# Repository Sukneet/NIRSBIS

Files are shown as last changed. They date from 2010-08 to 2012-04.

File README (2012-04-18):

Design of a Near Infrared Spectrophotometry Brain Imaging System

Measuring brain activity is at task generally left for EEG or fMRI. However, there is a lesser known imaging technique known as near infrared spectrophotometry in which near infrared light is shone into the patients head to measure changes in oxygenation that directly relates to brain activity. This paper describes a low-cost, wireless, portable near infrared spectrophotometry system that is able to measure brain activity. The results show that not only is the system able to measure changes in brain activity relating to motor movement, visual stimulation, and intense thinking, but it is also able to measure muscle activity.

My final year capstone project. Hosted for archival reasons.

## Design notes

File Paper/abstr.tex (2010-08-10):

\prefacesection{Abstract}

Measuring brain activity is at task generally left for EEG or fMRI. However, there is a lesser known imaging technique known as near infrared spectrophotometry, in which near infrared light is shown into the patients head to measure changes in oxygenation that directly relate to brain activity. This paper describes a low-cost, wireless, portable  near infrared spectrophotometry system that is able to measure brain activity. The results show that not able is the system able to measure changes in brain activity relating to motor movement, visual stimulation, and intense thinking, it is also able to measure muscle activity. 

\vspace{10mm}

\noindent Keywords: near-infrared spectroscopy, brain activity, functional monitoring and imaging, imaging, optical imaging

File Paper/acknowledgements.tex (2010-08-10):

\prefacesection{Acknowledgements}

The author would like to thank Dr. Doyle, this project's faculty adviser, for his various advice and directions. Texas instruments deserves acknowledgement for supplying samples of the microcontroller, LDO regulator, monolithic photodiode, and other components. Dupont generously supplied a large sample of Pyralux flexible PCB. Additionally, the author would like to thank Atsuko Sugahara, at Marubeni Corporation, for spending the time to find the required infrared LEDs and allowing for the purchase of them in low quantity. 

The developers behind the mspgcc project deserve a large thank you for porting the GCC toolchain to the MSP430 and creating various helpful programs. The developers at TinyOS also deserve acknowledgement for creating the software to program the MSP430 through its bootloader.

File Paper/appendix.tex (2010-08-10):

\appendix

\chapter {Calculations}

\section {Minimum UART speed calculation}

Given 2 sensors and a time resolution of 10ms (refer to Figure 4.9),

\begin{equation}
\frac{10\ ms}{12\ parts} \div 4\ parts = 4800\ Hz
\end{equation}
\begin{equation}
\frac {4800} {s} \times 16\ bits = 76\ 800\ bit/s
\end{equation}

\section {DPF calculation}

The differential path length factor (DPF) can be calculated from the following equation \cite{rosen05}

\begin{equation}
DPF^\lambda = \frac{1}{2}\left(\frac{3\mu_{s}^\lambda}{\mu_{a}^\lambda}\right)^{1/2} \left(1-\frac{1}{1+d(3\mu_{s}^\lambda\mu_{a}^\lambda)^{1/2}}\right)
\end{equation}

The absorption ($\mu_{a}^\lambda$) and reduced scattering ($\mu_{s}^\lambda$) coefficients cannot be directly measured by near infrared light, so the values given in past studies will be used. Specifically, $\mu_{a}^{730nm}$=0.015 mm$^{-1}$, $\mu_{a}^{850nm}$ = 0.023 mm$^{-1}$, $\mu_{s}^{730nm}$= 0.80 mm$^{-1}$, and $\mu_{s}^{850nm}$=0.95 mm$^{-1}$. The values at 750nm could not be found, so the values at 730nm will be used. Plugging these values into the equation above gives, $DPF^{730nm}$=5.0055 and $DPF^{850nm}$=4.6564.

\chapter{Flow Charts}
\section {Microcontroller code flow chart}

\headsep = 5pt
\begin{figure}[htp]
\centering
\caption{Microcontroller code flow chart}

\end{figure}

\begin{figure}[htp]
\centering

\end{figure}

\begin{figure}[htp]
\centering

\end{figure}

\begin{figure}[htp]
\centering
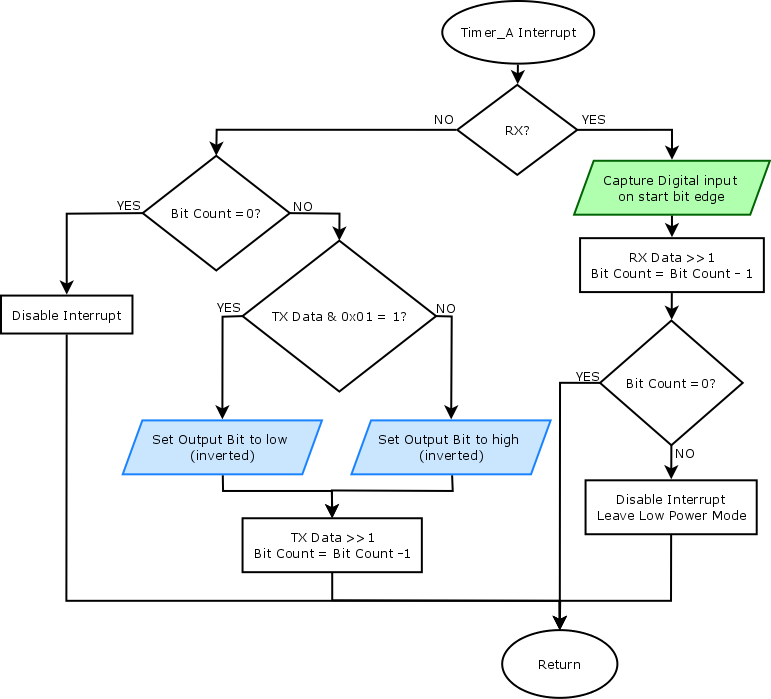
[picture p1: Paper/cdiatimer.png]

\caption{Timer\_A interrupt flow chart}
\end{figure}

\headsep = 0.5in

\chapter {Matlab Source Code}
\lstinputlisting[language=Matlab,breaklines=true]{filter.m}

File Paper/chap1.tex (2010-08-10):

\chapter{Introduction}
\section{Background}
Near-infrared spectrophotometry (NIRS) is a non-invasive imaging technique that can be used to measure brain function. It provides a higher spatial resolution than EEG or MEG without subjecting the patient to radiation in PET or having the low temporal resolution in fMRI scans \cite{wolf08}. NIRS systems are also considerably more portable than PET or fMRI scanners without the messy string of wires involved with EEG or MEG. As such, they can be used on bed-ridden patients where transportation is not possible. NIRS systems can also be used for long periods and are not directly susceptible to electro-magnetic interference  \cite{wolf08}.  \cite{wolf08} provides a good discussion about the principles, applications, and technologies of NIRS. 

A NIRS system for measuring brain activity is of particular interest in neonatal brain activity measurement where fMRI is not recommended for use \cite{wolf08}. Such systems allow for the quantification of the haemodynamic response of the cortex to visual, tactile, or auditory stimuli \cite{mini08}.  

NIRS works on the principle that light passing through a tissue is variably attenuated depending on the constitution of the tissue \cite{wolf08}. A near-infrared light source (within the spectra 700nm - 900nm) is placed onto the tissue. The re-emergent light is then picked up by a detector and the light intensity is measured. Varying levels in oxyhaemoglobin (O$_{2}$Hb) and  deoxyhaemoglobin (HHb) cause the optical properties of the tissue to vary; the absorption and scattering of light passing though the tissue changes. NIRS is very sensitive to these changes and is, thus, able to measure the haemoglobin concentration in the order of per mills \cite{wolf05}.

NIRS is able to pick up fast neuronal signals and slow haemodynamic signals. It is currently the only available imaging technique that is able to detect both signals, which is its main advantage. Fast neuronal signals are changes directly associated with neuron activity. The response typically arrives within 200ms. Slow haemodynamic signals are changes in haemoglobin concentrations caused by an increase in local oxygen use and subsequently blood flow due to brain activity \cite{mini08}. Fast neuronal signals are typically measured by EEGs, while slow haemodynamic signals are typically measured by fMRI.

A Near-Infrared spectrophotometry system was selected as this paper's subject because it combines three of the author's interests; imaging, optics, and the brain. Additionally, the project could be done fairly cost effectively, costing roughly \$200-300.

\section{Definition}
The main scope of this project is to measure brain activity in a patient. In order to do this, near infrared spectrophotometry will be used, wherein near-infrared light is shown into the patient's head to measure changes of oxygenation that directly relate to brain activity.

The objective of this project is to design a near infrared spectrophotometry (NIRS) system for the measurement of brain activity in localized areas in the brain. A prototype of the design will be built and wirelessly interfaced with a computer. The time-varying haemodynamic signals will then be plotted on the computer versus time. 

It is important to note that the results will be qualitative rather than quantitative as a device that correctly measures the optical properties of the patients skin, skull, fat, etc is not in the scope of this project. Since these optical properties vary based on skin pigmentation, age, gender, and many other factors, such a device is needed to obtain exact quantitative measurements. However, without this device a NIRS system can still measure varying haemodynamic signals. The absolute haemodynamic signal values will be irrelevant, the change in the haemodynamic signals over time are the relevant measurements. 

Since a major target of NIRS systems are neonatal infants, it is critical to minimize distress by performing the measurements as comfortably as possible due to the frailty of newborns \cite{mini08}. This is achieved by not having wires attached from the system to a computer, so as to not confine movement. Additionally, since neonatal infants are small, the system should also be small and light to restrict the infant as little as possible. As such, the device should be portable, light, small, and wireless. 

Additionally, a portable, light, small, wireless device allows the device to used on freely moving subjects. This allows the device to measure brain activity in athletes during exercise, subjects in social environments, and in animals.  

As with most projects, especially at the undergraduate level, it is important to keep costs down. Since NIRS systems for brain imaging is a fairly new field with no currently available commercial systems, low-cost devices will help to bring NIRS devices to the general population. In order to compete with current EEG systems, the device has to be fairly cheap and affordable. Therefore, while many early NIRS systems required the use of lasers, this project will focus on using low-cost LEDs.

Safety is always a concern in any device, specifically in medical equipment. The use of LEDs help to make NIRS systems suitable for clinical environments. The use of Lasers in early systems brought in safety concerns pertaining to damage the eye.

Thus, this project will focus on building a prototype of a low-cost wireless, portable NIRS system that is able to measure the change in haemodynamic signals.

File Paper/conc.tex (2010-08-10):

\chapter {Recommendations}

There are quite a few improvements that can be made to the system that were mainly not implemented due to time constraints and/or unexpected problems.

LED light and photodiode insulation is a topic that was not addressed in this system. To increase the SNR of the system it is advisable to block outside sources of light from interfering with the measurements or light sources. It is advisable to use some form of black insulation to absorb the outside light rather than reflect it to reduce scattering and increase SNR. 

One way of doing this is to apply black epoxy around the LEDs and photodiodes sufficiently to block light leakage and external light. However, sourcing medical grade black epoxy is not an easy task; it is hard enough finding normal black epoxy. It is possible to add a pigment to white epoxy, but this is no easy task either. An alternative is to use some kind of black foam or mesh.

The design of the sensor is not ideal. If it were to be revised a double-sided PCB would be used or the sensor would be made larger to reduce the number of jumper wires. This would help to make the sensor more robust and make building the sensor easier. Additionally the traces would be made larger to reduce the chance of breakage when flexed. 

The LEDs do not rest against the patient's skin when the sensor is placed against the patient. This reduced the SNR of the system by allowing light in from outside sources and decreases the light intensity before reaching the area of interest. This was the unattended side-affect of using SMD LEDs with the OPT101 monolithic photodiodes. Perhaps the use of standard SMD photodiodes or non-SMD LEDs would fix this. However, the use of standard SMD photodiodes would require the addition of a transimpedance amplifier. Finding non-SMD LEDs would be hard task, the SMD LEDs were selected in this project because that was all that could be acquired for a reasonable price. 

Attaching the sensors to the patients head was not addressed in this project. This is more or less a luxury. For the testing phase it is somewhat sufficient to hold the sensors to the head by hand. This will not be suitable for the final product though; any movement from the area of interest will add noise into the measurements. Thus, current ideas for achieving this would be using something like a headband or hairband to hold the sensor down; something that would provide enough pressure to ensure the sensor doesn't move while still allowing comfort for the patient.

Currently, this microcontroller uses BJTs to control the infrared LEDS. Should a second revision be done, an LED driver which controls the LEDs by PWM (pulse width modulation) would be used rather than simple BJTs. This will increase the efficiency of the system and allow greater control over the LEDs. This would allow for more localized measurements and power savings. Being able to control the brightness of the LEDs can be very advantageous for a versatile system. It does, however, come at the cost of complexity and thus time.

The overall system would greatly benefit if the system could display the data in real time. This is not very hard to do, just time consuming. Though having this would be of great benefit in a clinical environment where seeing the results the as fast possible may save life. 

Perhaps the greatest downfall of this project was trying to accomplish too much in a short period of time. The author took on the task of designing everything from scratch. This may have been detrimental to the overall result of the project. Rather than spending time on correctly displaying the results or ensuring the system work correctly all the time, time was spent make the microcontroller. It probably would have been beneficial to the project to have used an existing embedded system and focus more on the overall result. However, the knowledge gained has been invaluable to the author and the experience obtained designing the microcontroller will more likely be more beneficial to the author in the long run.

\chapter {Conclusion}

Despite these limitations, a fairly low-cost, wireless portable Near Infrared Spectrophotometry system was successfully built that is able to measure haemodynamic signals. The results shown by the NIRS device created in this project are promising. It was able to measure brain activity in the brain not only during motor activity, but during intense thinking and visual stimulation. The results are fairly promising as well, there is a strong correlation between brain activity and the measurements taken. In addition, it is also able to directly measure muscle activity, which was an unexpected bonus. 

While NIRS devices are currently still in the research phase with very few commercial systems, it is hard to see it ever successfully replacing EEG or fMRI measurements. EEG systems have a very large marketshare with commercially available system everywhere for very cheap and have a slightly higher temporal resolution than NIRS. fMRI has a much higher spatial resolution than NIRS, at the cost of temporal resolution, but there are many times researchers or doctors need to see brain activity deep into the brain. Laser NIRS systems can penetrate deeper than LED based ones, but at an increased cost, complexity, and loss of portability. However, there is that niche market where EEG does not cut it due to electromagnetic interference or a device with spatial resolution is required but fMRI is deemed to costly, is unable to be used due to long waiting lists, or in the case the patient cannot be transferred to the MRI machine. For this niche market, NIRS is their saviour.

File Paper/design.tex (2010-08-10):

\chapter{Design Procedures}

To create the NIRS system, a sensor consisting of LEDs, to emit light through the area of interest, and photodiodes, to convert the transmitted incident light into an electrical signal, must be made. The signal from the photodiodes must then be connected to an ADC in order to convert the analog signal to a digital signal that is readable by the computer doing the calculations. The digital signal must then be transmitted to the computer where calculations would be done.

To control the LEDs and convert the analog signal to a digital one, a microcontroller will be used. The microcontroller will then be interfaced to a computer through UART, initially through USB, then finally wirelessly through Bluetooth. The overall system can be seen in Figure 4.1.

\begin{figure}[htp]
\centering
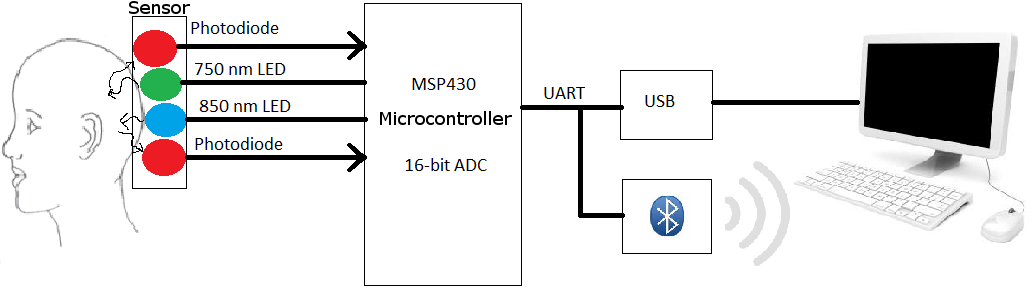
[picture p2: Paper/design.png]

\caption[A very basic overview of the system.]{A very basic overview of the system. For the testing phase, USB will be used to communicate with the computer. Eventually, Bluetooth will be used as the primary means of communication.}
\end{figure}

Bluetooth was selected over a low power wireless interface, such as ZigBee, due to Bluetooth being widely available on all modern phones. It was the intention to interface the device with a mobile phone, time permitting. However, this was never done. Bluetooth consumes much more power than other competing wireless communication systems, so to obtain optimum battery life it is not ideal. Had the author realized that there would be no time to interface the device with a mobile phone, a lower power wireless communication system would have been selected, most probably ZigBee.

To design the NIRS system, it was decided to design everything from scratch. The microcontroller circuit, the sensor, as well as the software was designed and built/written. This was done to truly test the author's knowledge obtained from his years at McMaster University. Additionally, this project provided an excellent chance to be introduced to microcontroller circuit design.

Development of this system began with the microcontroller, since nothing would work without it, followed by the sensor, then finally the software.

\section{The Microcontroller}

The microcontroller selected for use in this project is the Texas Instruments MSP430, specifically the MSP430f4250. The MSP430 was chosen due to its low power requirements and 16-bit sigma-delta ADC. In most cases, a 12-bit ADC would be sufficient, but a higher resolution will allow for the weak temporal signals to be detected easier. The MSP430 is also fairly cheap. These characteristics make it ideal for this project and made it standout from other competitors. 

While the MSP430f4250 is slightly excessive for this project, due to its built in LCD controller and array of I/O ports, it was the cheapest MSP430 model that the minimum required I/O ports and a 16-bit ADC.

While the MSP430f4250 does not have any dedicated UART hardware on-board, a software timer UART is sufficient in this project. The project only requires samples to be transmitted from the microcontroller to a computer. It was decided that flow control was not necessary for this project. This decision, however, led to many problems during testing, which will be discussed later. 

To design the microcontroller circuit, datasheets, user guides, application notes, and reference designs were read and used as a basis. Thankfully, the MSP430 has many built in capacitors and resistors (for example, adjustable oscillator capacitors) that help to reduce the overall components of the  build. The schematic of the device can be seen in Figure 4.2

\begin{figure}[htp]
\centering
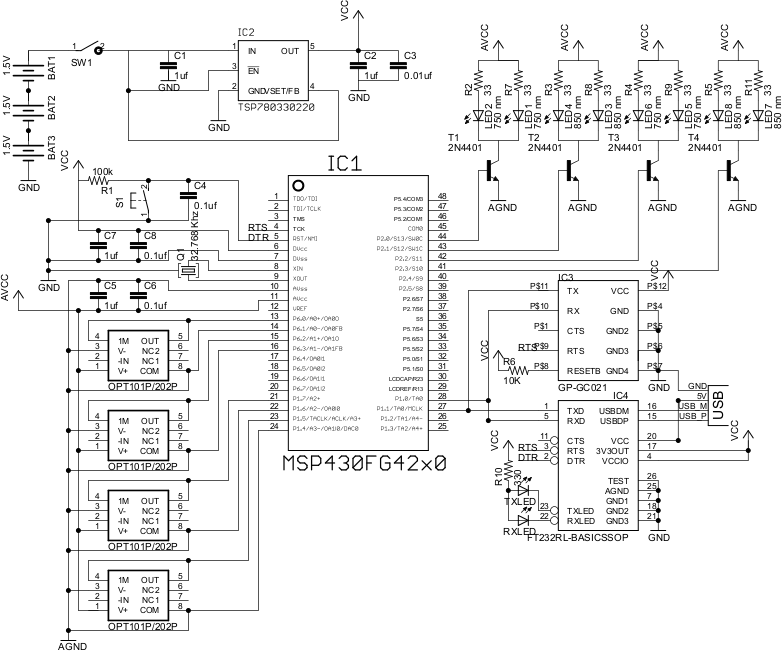
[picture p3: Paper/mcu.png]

\caption[Schematic of the system]{The schematic of the overall system. Note that two sensors are included in the diagram. The TPS79433 LDO regulator was used instead of the TPS780330220 in the diagram}
\end{figure}

A 32.768 Khz crystal is used because that is the only crystal the MSP430f4250 is designed to use. It is used as somewhat as a watchdog timer, waking the MSP430 up at select intervals to see if there is work to be done, unless it is told otherwise. Capacitors between VCC and GND were placed as close the the microcontroller as possible, as per Dr. Doyle's suggestion. This helps to reduce any noise that may have been picked up between the power supply and the microcontroller. This is especially a problem with the MSP430, any fluctuations/noise in the power supplied to it will cause the ADC to be very noisy. This is perhaps the main reason why the MSP430 is not very popular in projects that require signal acquisition. However, with proper consideration, this should not be much of an issue. To further reduce the noise in the ADC, separate power and ground are used for digital signals and analog signals, VCC \& GND and AVCC \& AGND respectively. 

The frequency the microcontroller operates at is governed by the voltage supplied by its power supply. Since the Bluetooth module operates at 3.3V and the USB UART device outputs power at 3.3V when powered by USB, a 3.3V power supply was selected. This sets the frequency of the microcontroller to ~7 Mhz, which is set by a FLL (frequency-locked loop). The speed the microcontroller operates at is of no big importance in this project. The sampling rate for data acquisition is slow enough, at 100Hz, that the 32Khz crystal is fast enough to supply the clock at which to sample the data. The speed of the UART is what is affected by the microcontroller speed. It was determined that the speed of the UART must be at least 76 800 bit/s or 76.8k baud (see Appendix A), which is easily exceed with a clock ~7Mhz.

To supply this voltage, 3 AA batteries connected to a regulator were chosen for long battery life. An LDO (low-dropout) regulator was selected over a more traditional regulator, such as an LM317. An LDO regulator was chosen because LDO regulators are highly efficient, consume very little power, and have low quiescent current, increasing battery life. Due to the the low power-requirements of every component, not much current is required by the system, making an LDO regulator ideal for use. LDO regulators are limited to the amount of current they can output due to consuming very little power.

The LDO regulator selected to do the job is the Texas Instruments TPS79433. It outputs voltages at 3.3V at a maximum current of 250mA. Additionally, it can be supplied power at less than 3.3V and will still output power at 3.3V. This is a nice feature because when the batteries drain to below 3.3V, the unit will still be operational. This regulator was selected because it meets all the requirements and free samples were obtainable from Texas Instruments. The circuit for the power supply was derived from the datasheet. 

To interface with the computer, the an USB to UART device was used. The FTDI FT232 was selected due to many good reviews on the device and good compatibility with Linux and Windows. The circuit design is based on the reference design given in the datasheet. One thing to note is that, while the built-in bootloader implemented flow control, which was necessary to invoke the bootloader, the software UART used in this project did not. As such, the DTR wire had to be disconnected from the microcontroller when not programming the device. Otherwise, the DTR wire would reset the device when communicating with the computer. The USB UART interface was used to program the device and initially communicate to the device during testing.

Once everything was deemed working, the Bluetooth module was added to interface with the computer. The Bluetooth module selected was RF-BTMX417 by MDFLY. This was selected due to its cheap price, Bluetooth 2.0 specifications, and low power requirements. The design for the Bluetooth module was based on the reference design in the datasheet.

Once all the parts were selected, the majority of the necessary parts were ordered from Digikey due to their cheap prices. Free samples were obtained of the microcontroller and LDO regulator from Texas Instruments. The Bluetooth module was ordered from ebay. The prototype was built on a breadboard using SMD to DIP adaptors for each component needing one. The prototype can be seen in figure 4.3

\begin{figure}[htp]
\centering
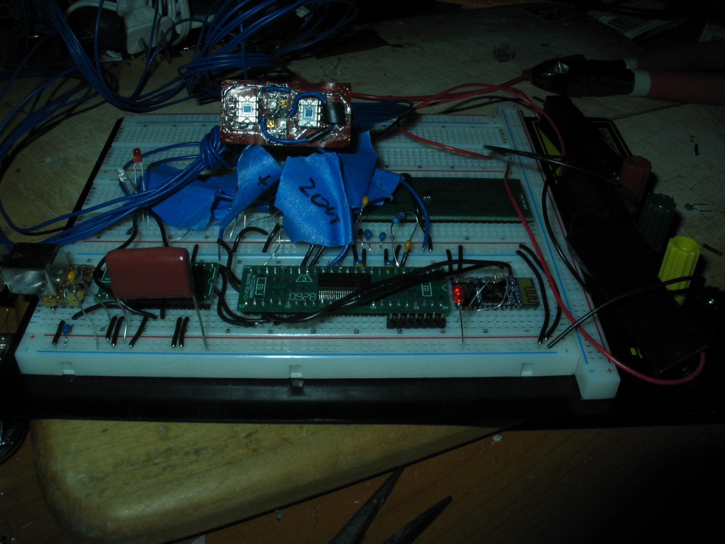
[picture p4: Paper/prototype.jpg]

\caption[The Prototype]{Picture of the prototype}
\end{figure}

To program the device, the MSP430f4250 has a a built-in non-overwritable (without JTAG) bootloader that can be programming over UART. A JTAG programmer would have cost at least \$100, greatly increasing the cost of this project, though making debugging much easier. The mspgcc tools included software, written by developers at TinyOS, to write to the bootloader on the MSP430. The mspgcc toolchain was used to compile the software, specifically mspgcc-4.4.3, and then programed to the device using the TinyOS software.

\section{The Sensor}

The sensor was first designed by selecting the components. The main problem was sourcing the LEDs with the desired wavelengths. After many emails to various distributors and manufactures, it was discovered Marubeni Corporation sold 750nm SMD LEDs in low quantities. The epitex SMT750-25 to be exact. As such, 750 nm LEDs were selected as one light source.

The wavelength of the other LED light source, must be above 800nm and be such that it minimizes interference between the two LEDs. Based on the study done in [4], the LEDs with wavelengths of 750nm and 850nm were selected to minimize interference between each LED. The 750nm wavelength responds better to deoxygenation in the blood and the 850nm wavelength responds better to oxygenation in the blood. Luckily enough, the 850nm LEDs were easily sourceable from Digikey in SMD form. The OSRAM SFH4650 being the only 850nm LED easily obtainable, or rather only 800 - 870nm SMD LED easily obtainable. The OSRAM SFH4650 has very recently been replaced by the more efficient SFH4651, while still providing similar specifications.

Unfortunately, the spectral half width of the LEDs are broader than desired. The 750nm LEDs have a spectral half-width of $\pm$ 35nm. While the 850nm LEDs have a spectral half-width of $\pm$ 42nm. This means the effective wavelength may vary by the spectral half-width, causing cross-talk between the LEDs and possibly throwing off the calculations. They have narrow halfangles, however, $\pm$ 25$^\circ$ and $\pm$ 20$^\circ$, respectively, which is desired to limit light leakage and force the highest light intensity towards the area of interest. With a forward current of 100mA, it is assumed the approximate penetration depth of these LEDs is 1cm, based on past studies \cite{rosen05}.

The LEDs are the most power-hungry device in this system. They could not be directly driven by the microcontroller. NPN transistors were selected to do this task. Specifically, the 2N4401 600mA NPN general purpose transistor. The 2N4401 was selected as it was the cheapest transistor available at Digikey with greater than 200mA continuous collector current. Each led has a maximum forward current of 100mA, so to power the LEDs at their maximum intensity, a 200mA transistor would be needed. The microcontroller would turn the NPN transistor on when it was desired to turn its subsequent LED on. Setting the Base of the NPN transistor to high, would allow current to flow from the Collector to the Emitter. Setting the Base to low (GND), would stop the current from flowing from the collector to the emitter. For a high integration density, each sensor and each transistor would have 2 LEDs of the same wavelength. This can be seen in Figure 4.4.

\begin{figure}[htp]
\centering
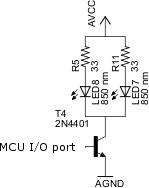
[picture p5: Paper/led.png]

\caption[LED control diagram]{The schematic of controlling one wavelength of LED on the sensor}
\end{figure}

To detect the reflected light back, a photodiode must be used. However, the electrical signal measured by a photodiode varies in current, opposed to voltage as most ADCs work. As such, the current must be converted into corresponding voltage by a transimpedance amplifier. An interesting solution to this problem is the OPT101 by Burr-Brown. It is a monolithic photodiode with a built-in transimpedance amplifier, all in a small DIP-8 package. This makes it ideal for this project. Two photodiodes are placed on each sensor to pick up scattering and increase the overall surface area of the detectors.

The overall design of the sensor can be seen in Figure 4.5. It was decided that the transistors would be put on the PCB rather than on the sensor to reduce the size of the sensor.

\begin{figure}[htp]
\centering

\caption[Sensor schematic]{The schematic of one sensor.}
\end{figure}

\subsection {Building the sensor}

Building the sensor was a daunting and hard task. The sensor had to be flexible to adhere to the head of the patient. As such, a flexible PCB is desired over a ridged one. 

To create the flexible PCB, the toner transfer method of homemade PCB creation was used. The PCB mill in the IEEE student Branch is not able to mill such a thin layer of copper on a flexible surface, and especially not with such thin tracings. 

The basic idea behind the toner transfer method is to print the design onto glossy paper using a laser printer. Melt the toner onto the copper board using an iron or something equally hot. Then etch the board using an enchant such as Ferric Chloride. Then to remove the toner from the PCB using a solvent such as acetone.

Dupont generously supplied a sample of dual sided Pyralux Copper PCB. However, making dual sided PCBs is no trivial task using the toner transfer method. My initial attempts to do so proved fatal. As such, one side was used a a ground plane, while the other side was etched. Since the LEDs were surface mount, all the devices had to be surface mount, unless they were to be mounted on the opposite side. 

To create the toner mask, Cadsoft EAGLE was used. The schematic was laid out in EAGLE, then the PCB designed. The idea was to minimize the size, keep the LEDs as close to the photodiodes as possible, and keep the parts somewhat symmetric to its double, while only making traces on one side. This layout sets the source-detector distance to be about 1cm (needed solve equations 3.7 and 3.8). The result can be seen in Figure 4.6.

\begin{figure}[htp]
\centering
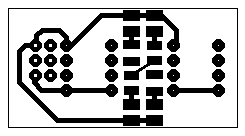
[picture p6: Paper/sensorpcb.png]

\caption[Sensor pcb layout]{The pcb layout of the  sensor, not mirrored.}
\end{figure}

The layout was then mirrored and printed out onto thick glossy photo paper (Staples Photo Plus Gloss Paper to be exact) using a Brother laser printer with toner usage set to high. The Brother laser printer is all that I had on hand, an older model laser printer would have been ideal since the Brother laser printer toner have a high melting point, making it hard to melt the toner from the paper onto the copper. The glossy paper was then placed onto the copper board and ironed with a standard household clothes iron set to high. The iron was left on for about 15 minutes. After which, the iron was removed and the copper board placed into water to separate the paper from it. After about 10 minutes, the remaining paper was peeled off of the copper board by hand. 

The toner was now stuck to the copper board. Any broken traces were touched up with a Sharpie marker. The opposite side (the ground plane) was coloured black to prevent the enchant from eating away at it. The board was then submerged in the etching solution (Ferric Chloride) to remove the exposed copper. After about 20 minutes, the exposed copper was removed and the board fully etched. The board was then rinsed off in water and cleaned up with acetone to remove the toner and Sharpie marker from the board. Any extra copper traces were scraped off. Solder was placed onto the copper traces to prevent oxidation and make soldering the components easier. The PCB was then complete as can be seen in Figure 4.7.

\begin{figure}[htp]
\centering
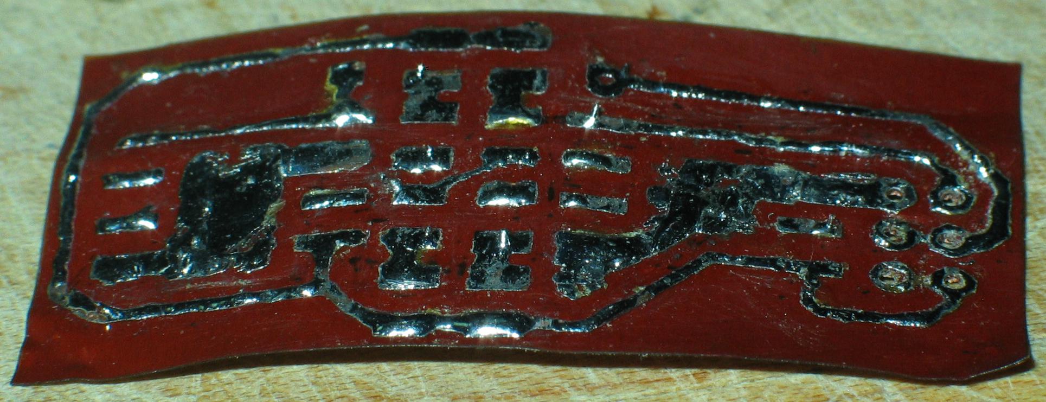
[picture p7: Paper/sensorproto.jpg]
\subfigure[Sensor after etching]{ }
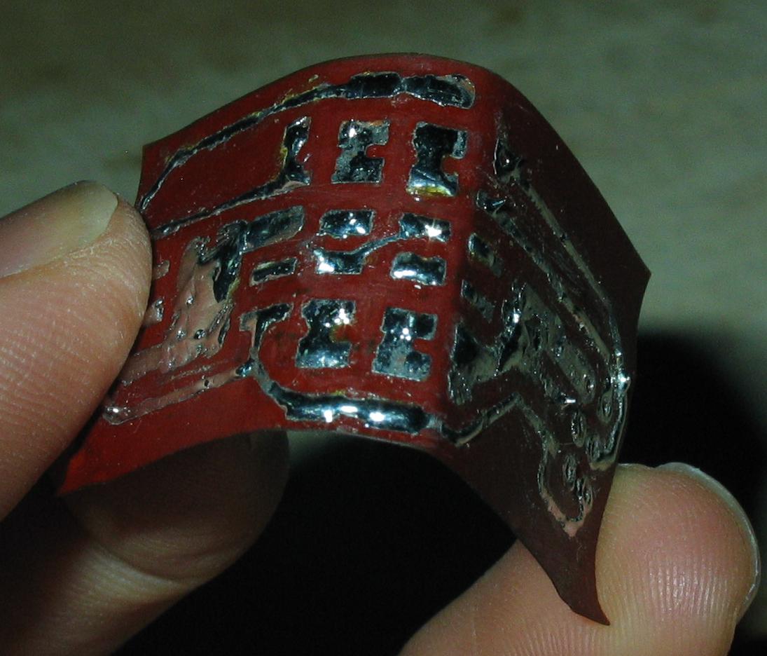
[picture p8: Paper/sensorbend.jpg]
\subfigure[Sensor showing flexibility]{ }
\caption[Sensor prototype PCB]{The completed sensor PCB}
\end{figure}

Unfortunately, I made the traces to thin. While the came out okay out of the etchant, after many bends, some traces broke (even though they appeared fine). 

Again, the majority of the electrical components were obtained from Digikey. With the exception of the OPT101 monolithic photodiode, which was obtained from Texas Instruments as a free sample. After populating the sensor and difficult task of adding jumper wires, the finalized sensor prototype was complete. Correctly building the board took quite a few hours to complete. The complete sensor can be seen in Figure 4.8. Due to time constraints only 1 sensor was built. Though, the microcontroller was designed to handle 2.

\begin{figure}[htp]
\centering
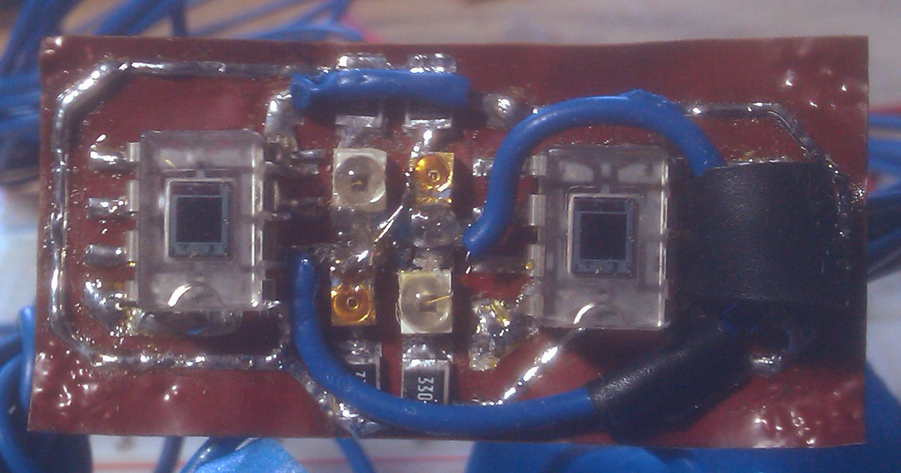
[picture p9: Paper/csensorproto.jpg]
\subfigure[Complete Sensor Prototype]{ }
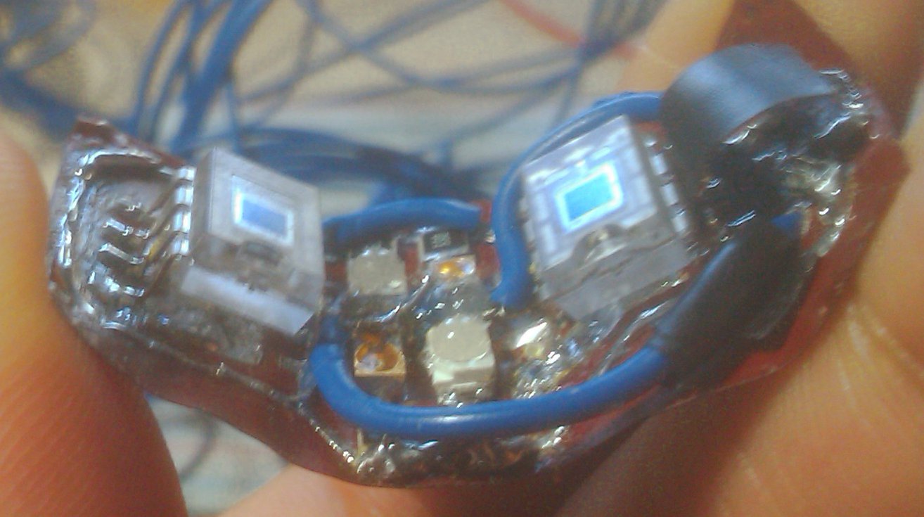
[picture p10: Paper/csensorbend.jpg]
\subfigure[Sensor Prototype showing flexibility]{ }
\caption[Finalized Sensor Prototype]{The finalized complete sensor}
\end{figure}

\section{Software}

To write the software for the microcontroller, C was selected over assembly to reduce development time and increase readability. As discussed above, the UART function had to be written in software in addition to data acquisition. To do this, example timer UART code by L. Westlund at Texas Instruments, available in the IAR Embedded Workbench example files, was used as a basis for the software UART functionality. This was done because the author did not know how to implement the UART functionality from scratch. Once UART was working, data acquisition was tackled.

\subsection{Data Acquisition}
Due to the slow haemodynamic response in your brain due to activity, a time resolution of 10ms (or 100Hz) is all that is needed. That is all the wavelengths and positions must be sampled at least every 10 ms.

To do this, data is sampled in a time multiplexed fashion. That is, all the data is sampled independently in a certain order within the time resolution. 

Firstly the sensors are sampled with all the LEDs off to obtain the background light intensity. Then the first wavelength of LED is turned on and allowed to stabilize for a period of time. Then the first signal is obtained from the first OPT101 photodiode, subtracted by the background light intensity, and transmitted to the computer.  Then the second signal is obtained from the second OPT101 photodiode, subtracted by the background light intensity, and transmitted to the computer. Then the LEDs are turned off, the second wavelength LEDs turned on, allowed to stabilize, and the cycle repeated. Once this cycle is completed, all the LEDs are turned off, the background light intensity sampled, and the cycle repeats. This is illustrated in Figure 4.9. Though, perhaps it is more easily seen in the microcontroller code flow chart in Appendix B.1.

\begin{figure}[htp]
\centering
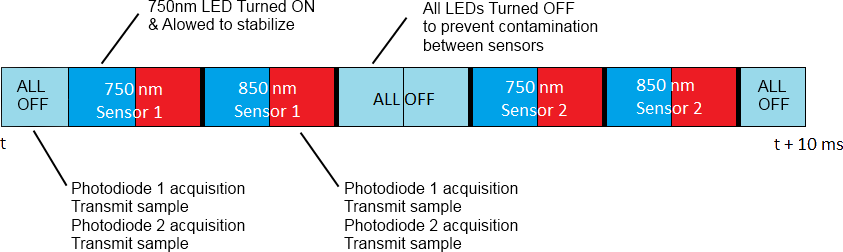
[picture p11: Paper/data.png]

\caption[Time multiplexed acquisition]{An illustration of the time multiplexed acquisition cycle.}
\end{figure}

\subsection {Computer Software}

To write the software, Ruby was selected as the language of choice. It was selected due to the author's desire to learn Ruby as it is a very popular dynamic general purpose object-oriented programming language. It is spoken highly of by many experienced computer science veterans. While not up to the speed of C or C++, Ruby has amazingly good performance for a dynamic programming language.

The computer software must firstly obtain the data from the device. To do this the serialport library from rubygems (a host of many Ruby librarys or 'gems') was used to interact with the serial port on the computer, communicating through UART. The serial port is opened, sent the message 'S', to message the device to begin acquiring data. The program then receives the data. The data is split into two parts the upper 8 bit and the lower 8 bits when it is received. The program combines them together and divides the resulting value by 0xFFFF. The reason for this is the output from the ADC on the microcontroller is relative to its maximum value of 0xFFFF. To ensure the data arrives correctly, an 'S' is transmitted by the device before sending each set of data to ensure that the device is synchronized correctly with the computer. Once all the data is received, the calculations are done on the raw data to obtain the necessary relevant values.

Equations 3.7 and 3.8 were used to calculate the change in concentrations. Equation 3.6 was used to calculate the differential optical density. During the project demonstration Equation 3.6 was not written correctly in the code, giving wrong results. This has since been fixed and the differential optical density is now calculated correctly. In order to calculate the change in concentrations, first the specific wavelength constant and differential pathlength factors must be found.

Since the specific wavelength extinction coefficient of the absorber($\epsilon^\lambda$) cannot be directly measured with near infrared light, they are found by interpolating the values given for these coefficients for oxyhaemoglobin and deoxyhaemoglobin in literature, specifically \cite{wray88} and \cite{roe91}. This results in $\epsilon^{750nm}_Hb$ = 1.532, $\epsilon^{750nm}_O2Hb$ = 0.600, $\epsilon^{850nm}_Hb$ = 0.781, $\epsilon^{850nm}_O2Hb$ = 1.097. Calculating the differential pathlength factor (DPF$^\lambda$) yeilds $DPF^{730nm}$=5.0055 and $DPF^{850nm}$=4.6564. The calculation for DPF$^\lambda$ can be seen in Appendix A.2.

Once the calculations are complete the change in concentrations are output to text files that can be read by Matlab. The data is very noisy and requires a low pass filter to be done on it to obtain the necessary data. Due to time limitations, a low pass filter was not able to be made in Ruby for the software. As such, Matlab was decided to be used to filter the data. As per \cite{wolf05}, a low pass filter with a cutoff of 0.5Hz should be used. Therefore a low pass fourth-order butterworth filter was used with a cutoff of 0.5Hz. The Matlab source code can be seen in Appendix C. Taking the Fourier transform of the data before filtering gives the result in Figure 4.10(a). Taking the Fourier transform of the data after filtering gives the result in Figure 4.10(b).

\begin{figure}[htp]
\centering
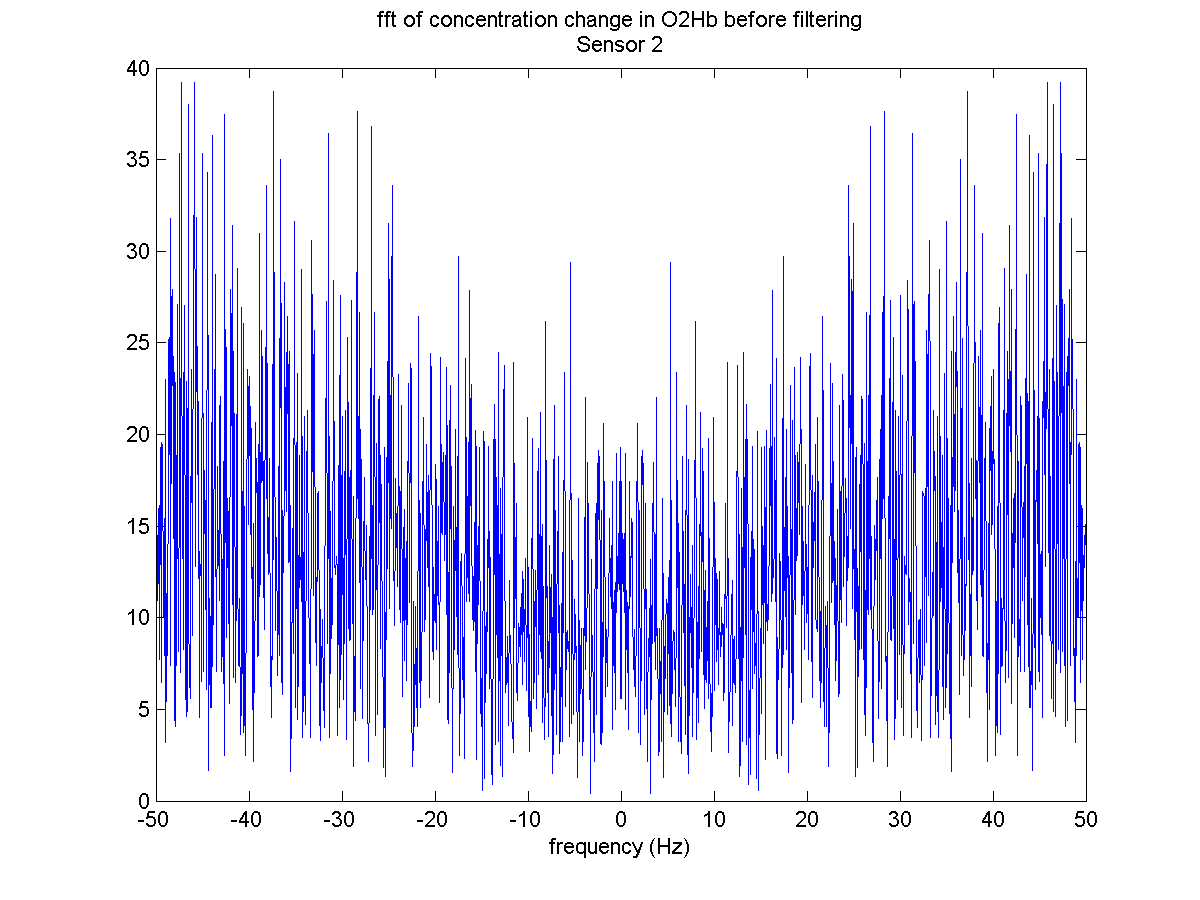
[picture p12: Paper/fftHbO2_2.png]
\subfigure[FFT of data before filtering]{ }
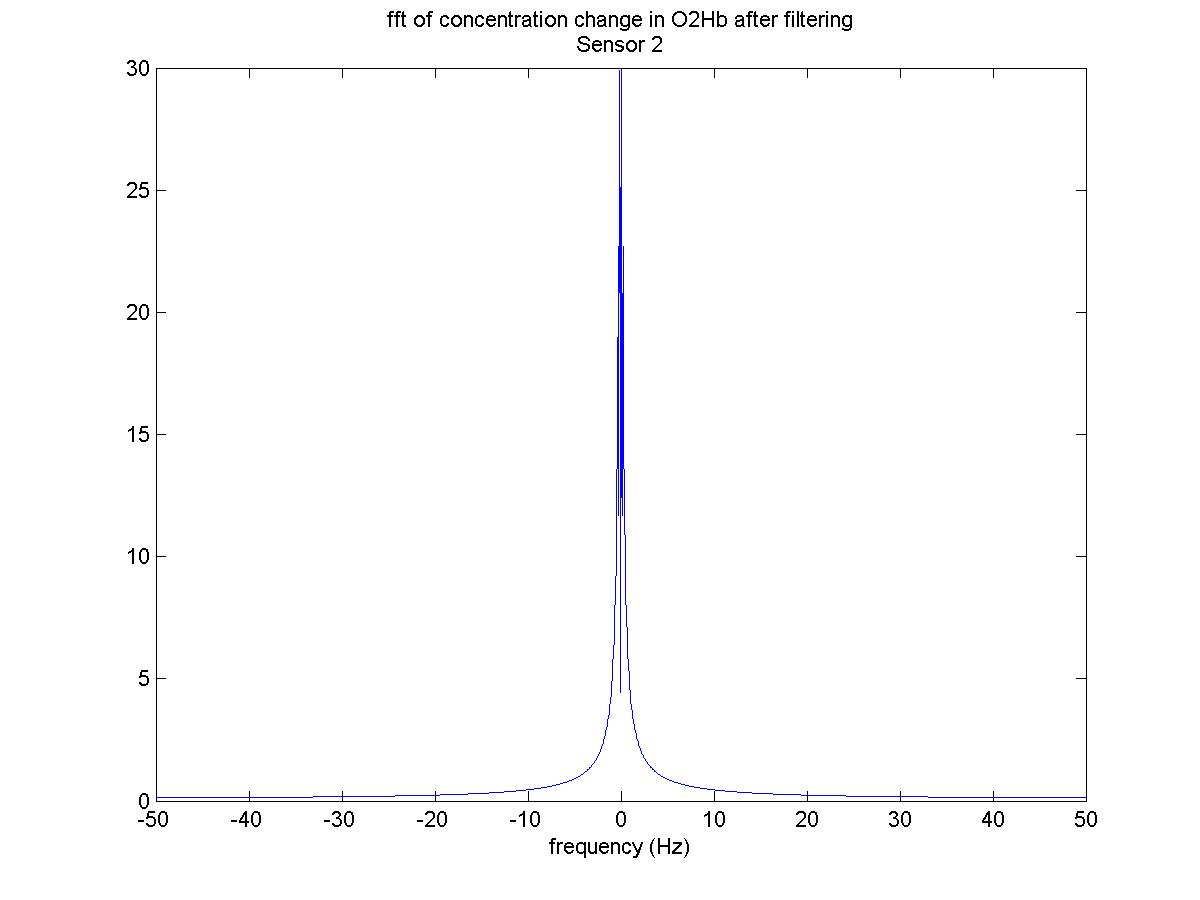
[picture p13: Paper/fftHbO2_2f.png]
\subfigure[FFT of data after filtering]{ }
\caption[FFT of data]{The FFT of the data before filtering and after filtering. The data used is the change in oxyhaemoglobin during motor movement}
\end{figure}

The design of the device is now complete and results can be seen.

\section{Cost}

Since one of the goals of this project is to low-cost, Table 4.1 shows the total cost to build one of these systems with one sensor. The USB to UART module will be left out since it is only needed for programming the device. In a mass produced system, the microcontroller would be programmed by JTAG anyway.

\begin{table}
  \caption{Cost of 1 NIRS System}
  \begin{tabular}{| l | c | r | r |}
\hline
\multicolumn{4}{|c|}{Cost of 1 NIRS System} \\
\hline
\bf Item & \bf Quantity & \bf Unit Price & \bf Total Price \\ \hline
LDO Regulator&1&\$1.85&\$1.85\\
1$\mu$f Capacitors&4&\$0.05&\$0.20\\
0.01$\mu$f Capacitors&4&\$0.01&\$0.04\\
32KHz Crystal&1&\$0.36&\$0.36\\
MSP430f4250&1&\$4.55&\$4.55\\
Power LED&1&\$0.10&\$0.10\\
330$\Omega$ Resistor&2&\$0.06&\$0.12\\
Bluetooth LED&1&\$0.12&\$0.12\\
Bluetooth module&1&\$18.00&\$18.00\\
SPDT Switch&1&\$3.99&\$3.99\\
2N4401 BJT&2&\$0.14&\$0.28\\ \hline
\multicolumn{3}{|r}{\em Subtotal}&\$29.61 \\ \hline
\multicolumn{4}{|l|}{\bf Sensor} \\ \hline
750nm LED&2&\$3.02&6.04\\
850nm LED&2&\$1.17&\$2.34\\
33$\Omega$ Resistor&4&\$0.17&\$0.68\\
OPT101 Photodiode&2&\$6.23&\$12.46\\ \hline
\multicolumn{3}{|r}{\em Subtotal}&\$21.52 \\ 
\multicolumn{3}{|r}{\bf \em Total}&\bf \$51.13 \\
\hline
  \end{tabular}
\end{table}

\section{Design Challenges}
The initial design challenges encountered were sourcing the LEDs. A consumer retailer could not be found selling LEDs of a wavelength between 700nm - 830nm. Many email had to be sent out to various manufacturers, retailers, and distributors until the Marubeni Corporation responded that they would be willing to sell some samples.

The Majority of the other design challenges stem from the author's inexperience with microcontroller design and time constraints. 

Perhaps one of the longest challenges that had to be overcome was the UART communication. After the prototype was built, it would not communicate over UART via the USB to UART module. After much troubleshooting and going over the design many times, comparing my circuit design to another MSP430 project that used UART, it was determined that the TX and RX wires were swapped. Originally the TX output from the USB UART module was connected to the TX output of the microcontroller and the RX input connected to the RX input. Due to inexperience, the author believed that the connection matched up rather than the logical way of TX to RX.

Now that the bootloader was able to be programmed, implementing the software timer UART was a daunting task. Writing custom code proved to be futile, so example code was turned to for the UART implementation. However, even unmodified sample code was not communicating to the computer. Code was executing correctly on the device, it was possible to to flash LEDs and such. However, once a serial terminal was opened on the computer, code would stop executing, as if it was stuck in an interrupt. Due to the decision to not use a JTAG programmer, debugging could only be done via LEDs. 

After many countless hours, it was realized that the DTR line on the USB UART module was setting RST to low on the microcontroller, resetting the device. The RST wire is there because it is needed to invoke the bootloader and is part of the flow control used by the built-in bootloader. However, it must be disconnected when not trying to invoke the bootloader.

The flexible sensor provided a great design challenge. If the  creation of the sensor was not difficult enough, populating the board was. Due to the decision to make the sensor as small as possible and being only a single sided SMD PCB, jumper wires were used to connect certain components. This made it a large pain to solder the components. Additionally, small traces were selected. Had the board been ridged rather than flexible, this design would have been fine since the traces came out okay. But after many bends and flexes, some of the traces broke, even if they appeared to be okay. These were easily fixable by soldering the traces back together. However, it provided a big headache when testing the device.

The computer software also played a somewhat large challenge and is perhaps the weakest part of this project and the main reason for its poor performance. Data acquisition played a problem at first. The microcontroller and computer were not in sync, and the computer received many null data points when trying to retrieve the data. However after properly matching the times between the two programs through the use of sleep functions, the data was retrieved correctly. The switch to the Bluetooth module removed these errors, everything synced up fine and the sleep functions code be removed. It is assumed that there are performance issues with the FTDI USB UART driver in Linux. However, the microcontroller still sends the char 'S' before each measurement to ensure everything syncs up fine.

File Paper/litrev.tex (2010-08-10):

\chapter{Literature Review}

While there are a variety NIRS devices out there, it is still very much in the research phase, though the theory behind it is well proven. Generally, there are two classes of NIRS systems used for brain imaging, LED based systems and Laser based system. All the original ones used lasers as a light source. However, as time moved on it was realized a cheaper, more convenient, safer alternative had to be found to be applicable in the clinical market. LEDs was the solution to this. They allows for a much cheaper system without the hassle of the optic cabling or the danger of lasers. Laser systems are still used today though, as they still provide advantages to LEDs. They have a much more narrow spectrum, allowing for more accurate results. They can emit a much stronger light intensity, allowing them to penetrate deeper into tissue. As such, two past NIRS devices will be discussed.

\section{Laser Based System}

Laser based NIRS system have been around for quite some time. However, there are still quite a few being designed today. One such design being designed quite recently can be seen in \cite{tor08}. The system is an Laser based multi-channel multi-wavelength NIRS system.

The advantage to on such design is it has a high acquisition frequency of 1 MHz, a very high sensitivity, a high penetration depth, a high spatial resolution, the ability to have up to 64 channels and 18 sources, and a high temporal resolution of 25 ps (higher than that of LEDs). One interesting thing about this paper is that is uses time-resolved NIRS sampling, opposed to the continuous wave NIRS sampling, most NIRS systems use. This allows the system to find the absorption and scattering coefficients individually. Continuous wave NIRS sampling can only find the combination of absorption and scattering coefficients.

The disadvantages to this system are basically the same as any Laser based system. It is highly expensive, requiring a spaghetti of optical wires (refer to Figure 2.1). The system is large an very much not portable. It is somewhat delicate, relying on Photomultiplier tubes.

\begin{figure}[htp]
\centering
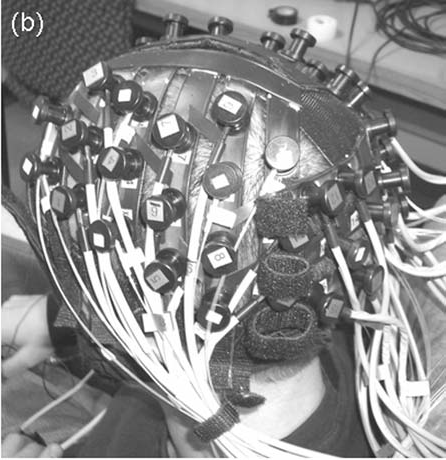
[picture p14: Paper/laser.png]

\caption[Laser NIRS System]{Picture of a probe used in a Laser NIRS system. Note that this is not the system described above. \cite{fran06}}
\end{figure}

\section{The MCP II}

The MCP II is a versatile, multi-channel NIRS instrument. It was designed in order to map neuronal activation in neonatal and adult brains in response to motor, tactile, and visual stimulation. It aimed to have high SNR, good spatial sampling, and good clinical useability and ease of transportation \cite{wolf05}.

The MCP II used three LEDs to calculate the change in concentration of oxyhaemoglobin and deoxyhaemoglobin, opposed to the more common dual wavelength approach. They also used PIN photodiode's with a very large activation area, with 7.5mm$^2$, as their detectors. This is a very good idea. PIN photodiodes are especially sensitive, but with the addition of the large activation area it allows for a higher SNR \cite{wolf05}. 

The sensor designed in this system is fairly interesting. A flexible sensor that was molded with a curvature was used to fit neonatal heads as well as adults. Silicon and SMD devices were used to prevent light leakage. Transparent silicon was also placed around the photodiodes to provide two optical windows \cite{wolf05}.

The system is such designed that it is able to use 8 sensors at one time, with the ability to simultaneously measure the light intensity at two detectors. The system uses time multiplexed data acquisition with an oversampling ADC of 12-bits, to achieve a 100Hz sampling rate. Interestingly, the system is coupled to a stimulation unit that provides tactile, acoustic, and visual stimuli to the patient to accurately measure brain activity \cite{wolf05}.

The MCP II achieved very good results, obtaining a high SNR, high sensitivity, good resolution, and a good clean signal, as can be seen in Figure 2.2. Additionally, it is very convenient to have a multi-channel system that can simultaneously capture two channels \cite{wolf05}.

\begin{figure}[htp]
\centering
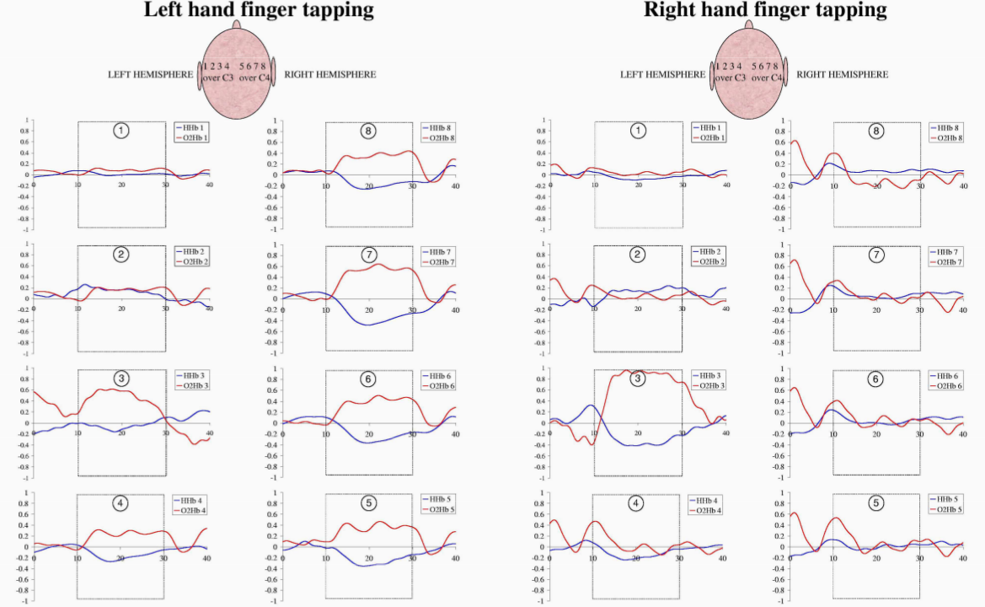
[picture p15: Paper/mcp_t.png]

\caption[MCP II Measuring Motor Movement]{The MCP II measuring brain activity in the motor cortex in relation to finger tapping. "Finger tapping exercises were performed from second 10 to 30 (dotted box). The first (sensors 1-4) and the second column (sensor 5-8) measured over left and right hemisphere respectively before, during, and after left hand finger tapping. The third (sensors 1-4) and fourth column (sensor 5-8) show the left and right hemisphere during right hand finger tapping. An activation typically consists of an increase in oxyhemoglobin (O2Hb) concentration and of a decrease in deoxyhemoglobin (HHb) concentration. The higher O2 consumption in the activated area is immediately overcompensated by an increase in blood flow, which leads to the observed pattern. Both hands showed a stronger contralateral activation on the motor cortex hemisphere. The ordinates are scaled to μ mol/l." \cite{wolf05}}
\end{figure}

While, the MCP II is this projects main influence, it does have some downfalls. The system is using an unnecessarily powerful processor, running Linux, just to provide wired network communication. A simple pic18 can be used to provide network communication and be much cheaper. Additionally, the system is wired, making the system not very portable. Additionally, while the system is 'portable', it is more less transportable, rather than portable. Due to the number of channels used and the complexity of the system, it is fairly large, though comparatively small compared to Laser NIRS systems. The ideas used in the system are not original, but they successfully chose a myriad of good ideas to implement an excellent working system.

\section{Wireless Miniaturized NIRS System}

There have been similar LED based system designed that are wireless, smaller, and lighter. These designs are basically simplified designs of the MCP II,  while producing comparable results to other NIRS systems. One such design is \cite{mini08}. The main aspect of this design was to produce an lightweight, small, wireless NIRS system to minimize distress when imaging neonatal infants.

The design is simple and efficient using a dual wavelength LED design. It uses a an Silicon Labs 8051 type microcontroller connected to a Bluetooth module for communication. It is also multi-channel based system the ability to connect up to 12 channels, though only four are connected in the literature \cite{mini08}.

The sensor design, though not ideal, is unique. They grouped together multiple LEDs of the same wavelength to obtain a high integration density. Additionally, black epoxy was placed around each photodiode and LED group to prevent light contamination and leakage. The sensor placement is odd however, having two channels facing opposing directions as the other two. This is perhaps the drawback of their design \cite{mini08}.

They are able to obtain decent performance however, obtaining comparable results to that of MCP II, as can be seen in Figure 2.3.

\begin{figure}[htp]
\centering
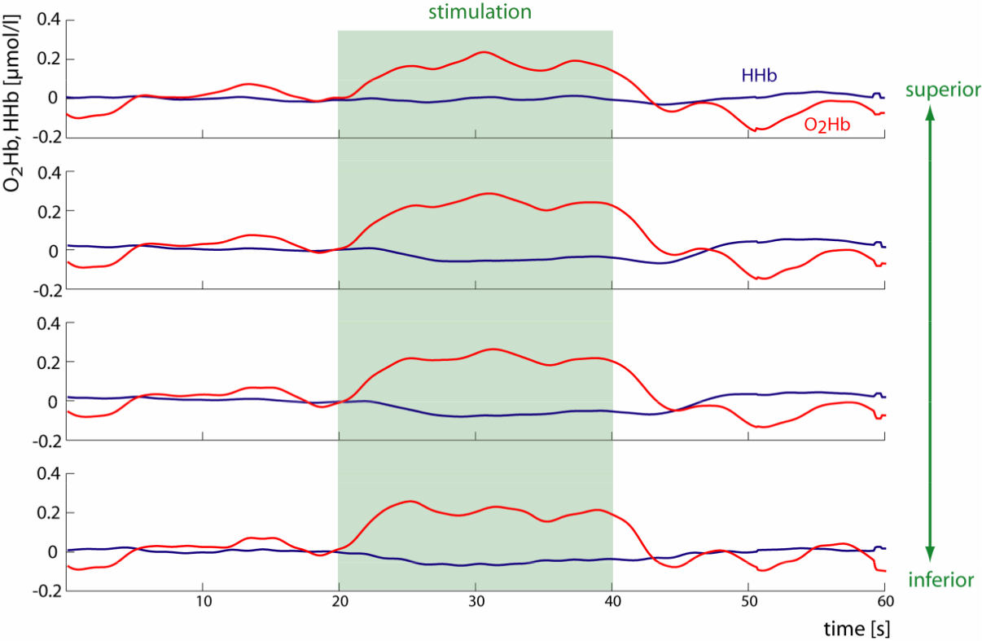
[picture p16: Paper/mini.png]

\caption[Wireless Miniaturized NIRS System Measuring Motor Movement]{TheWireless Miniaturized NIRS System measuring brain activity in the motor cortex in relation to finger tapping. "Averaged hemodynamic response of the cortex to finger tapping for four source-
detector positions." \cite{mini08}}
\end{figure}

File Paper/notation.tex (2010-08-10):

\prefacesection{Notation and Abbreviations}

\begin{tabbing}
\quad\= 123456789 \quad\= Functional magnetic resonance imaging\kill\\

  \> \bf ADC \> Analog-to-digital converter\\
  \> \bf DIP \> Dual in-line package, perhaps the most common through-hole\\
  \> \> mounted IC packaging \\
  \> \bf EEG \> Electroencephalography \\
  \> \bf GCC  \> GNU Compiler Collection, a compiler system by the GNU project \\
  \> \bf fMRI \> Functional magnetic resonance imaging\\
  \> \bf JTAG \> Joint Test Action Group, widely used for programming and \\
  \> \> debugging ICs.\\
  \> \bf HHb \> deoxyhaemoglobin, deoxygenated haemoglobin \\
  \> \bf LED \> Light emitting diode\\
  \> \bf LDO \> Low-dropout (regulator)\\
  \> \bf MCU \> Microcontroller \\ 
  \> \bf MSP430 \> Microprocessor platform of ultra-low power 16-bit RISC \\
  \> \> mixed-signal microcontrollers \\
  \> \bf mspgcc \> port of the GCC toolchain for MSP430 MCUs\\
  \> \bf NIRS \> Near-infrared spectrophotometry \\
  \> \bf O$_{2}$Hb \> Oxyhaemoglobin, oxygenated haemoglobin\\
  \> \bf PCB \> Printed circuit board \\
  \> \bf Ruby \> A dynamic general purpose Object-Oriented programming language\\
  \> \bf SMD \> Surface mount devices\\
  \> \bf SNR \> Signal-to-noise ratio
\end{tabbing}

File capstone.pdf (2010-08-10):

# Design of a Near Infrared Spectrophotometry Brain

# Imaging System

BY

SUKNEET BASUTA

Electrical and Biomedical Engineering Design Project (4BI6)

Department of Electrical and Computer Engineering

McMaster University

Hamilton, Ontario, Canada

### DESIGN OF A NEAR INFRARED SPECTROPHOTOMETRY

### BRAIN IMAGING SYSTEM

BY

SUKNEET BASUTA

Electrical and Biomedical Engineering

Faculty Advisor: Prof. Doyle

Electrical and Biomedical Engineering Project Report

submitted in partial fulfillment of the degree of

Bachelor of Engineering

McMaster University

Hamilton, Ontario, Canada

April 23, 2010

Copyright

c April 2010 by Sukneet Basuta

# Abstract

Measuring brain activity is at task generally left for EEG or fMRI. However, there

is a lesser known imaging technique known as near infrared spectrophotometry, in

which near infrared light is shown into the patients head to measure changes in

oxygenation that directly relate to brain activity. This paper describes a low-cost,

wireless, portable near infrared spectrophotometry system that is able to measure

brain activity. The results show that not able is the system able to measure changes

in brain activity relating to motor movement, visual stimulation, and intense thinking,

it is also able to measure muscle activity.

Keywords: near-infrared spectroscopy, brain activity, functional monitoring and imag-

ing, imaging, optical imaging

ii

# Acknowledgements

The author would like to thank Dr. Doyle, this project’s faculty adviser, for his

various advice and directions. Texas instruments deserves acknowledgement for sup-

plying samples of the microcontroller, LDO regulator, monolithic photodiode, and

other components. Dupont generously supplied a large sample of Pyralux flexible

PCB. Additionally, the author would like to thank Atsuko Sugahara, at Marubeni

Corporation, for spending the time to find the required infrared LEDs and allowing

for the purchase of them in low quantity.

The developers behind the mspgcc project deserve a large thank you for porting

the GCC toolchain to the MSP430 and creating various helpful programs. The devel-

opers at TinyOS also deserve acknowledgement for creating the software to program

the MSP430 through its bootloader.

iii

# Notation and Abbreviations

ADC | Analog-to-digital converter
DIP | Dual in-line package, perhaps the most common through-hole
| mounted IC packaging
EEG | Electroencephalography
GCC | GNU Compiler Collection, a compiler system by the GNU project
fMRI | Functional magnetic resonance imaging
JTAG | Joint Test Action Group, widely used for programming and
| debugging ICs.
HHb | deoxyhaemoglobin, deoxygenated haemoglobin
LED | Light emitting diode
LDO | Low-dropout (regulator)
MCU | Microcontroller
MSP430 | Microprocessor platform of ultra-low power 16-bit RISC
| mixed-signal microcontrollers
mspgcc | port of the GCC toolchain for MSP430 MCUs
NIRS | Near-infrared spectrophotometry
O2Hb | Oxyhaemoglobin, oxygenated haemoglobin
| iv

PCB | Printed circuit board
Ruby | A dynamic general purpose Object-Oriented programming language
SMD | Surface mount devices
SNR | Signal-to-noise ratio

v

# Contents

Abstract | ii
Acknowledgements | iii
Notation and Abbreviations | iv
1 Introduction | 1
2 Literature Review | 5
3 Theory | 12
4 Design Procedures | 18

vi

5 Results and Discussion | 40
6 Recommendations | 58
7 Conclusion | 61
A Calculations | 63
B Flow Charts | 65

vii

C Matlab Source Code | 70

viii

# List of Tables

ix

# List of Figures

2.1 Laser NIRS System | | 7
2.2 MCP II Measuring Motor Movement | | 9
2.3 Wireless Miniaturized NIRS System Measuring Motor Movement . . | 11
3.1 Propagation of photons | | 13
3.2 Propagation of photons | | 14
4.1 A very basic overview of the system | | 19
4.2 Schematic of the system | | 21
4.3 The Prototype | | 24
4.4 LED control diagram | | 27
4.5 Sensor schematic | | 27
4.6 Sensor pcb layout | | 29
4.7 Sensor prototype PCB | | 30
4.8 Finalized Sensor Prototype | | 32
4.9 Time multiplexed acquisition | | 33
4.10 FFT of data | | 36
5.1 Placement of Sensor to Measure Right Hand Movement | | 41
5.2 Left Motor Cortex Measurements with Motor Movement | | 42
5.3 Left Motor Cortex Measurements with No Motor Movement | | 44

x

5.4 Left Motor Cortex Measurements with Motor Movement, Test 2 . . . | 46
5.5 Placement of Sensor to Measure Left Hand Movement | | 47
5.6 Left Motor Cortex Measurements with Motor Movement | | 48
5.7 Placement of Sensor to measure Frontal Lobe | | 49
5.8 Frontal Lobe Measurements while Thinking Intensely | | 50
5.9 Frontal Lobe Measurements while Relaxed | | 51
5.10 Placement of Sensor to Measure Visual Cortex | | 52

5.11 Visual Cortex Measurements while Moving Eyes between focused objects 53

5.12 Frontal Lobe Measurements while Relaxed | | 54
5.13 Bicep Measurements with Continuous Flexion and Extension | | 55

5.14 Bicep Measurements with Continuous Fexion and Extension with a

Weight | | 56
B.1 Microcontroller code flow chart | | 66
B.2 Timer A interrupt flow chart | | 69

xi

# Chapter 1

# Introduction

## 1.1 Background

Near-infrared spectrophotometry (NIRS) is a non-invasive imaging technique that

can be used to measure brain function. It provides a higher spatial resolution than

EEG or MEG without subjecting the patient to radiation in PET or having the low

temporal resolution in fMRI scans [1]. NIRS systems are also considerably more

portable than PET or fMRI scanners without the messy string of wires involved with

EEG or MEG. As such, they can be used on bed-ridden patients where transportation

is not possible. NIRS systems can also be used for long periods and are not directly

susceptible to electro-magnetic interference [1]. [1] provides a good discussion about

the principles, applications, and technologies of NIRS.

A NIRS system for measuring brain activity is of particular interest in neonatal

brain activity measurement where fMRI is not recommended for use [1]. Such systems

allow for the quantification of the haemodynamic response of the cortex to visual,

tactile, or auditory stimuli [2].

CHAPTER 1. INTRODUCTION

NIRS works on the principle that light passing through a tissue is variably atten-

uated depending on the constitution of the tissue [1]. A near-infrared light source

(within the spectra 700nm - 900nm) is placed onto the tissue. The re-emergent light

is then picked up by a detector and the light intensity is measured. Varying levels in

oxyhaemoglobin (O2Hb) and deoxyhaemoglobin (HHb) cause the optical properties

of the tissue to vary; the absorption and scattering of light passing though the tissue

changes. NIRS is very sensitive to these changes and is, thus, able to measure the

haemoglobin concentration in the order of per mills [3].

NIRS is able to pick up fast neuronal signals and slow haemodynamic signals. It

is currently the only available imaging technique that is able to detect both signals,

which is its main advantage. Fast neuronal signals are changes directly associated

with neuron activity. The response typically arrives within 200ms. Slow haemody-

namic signals are changes in haemoglobin concentrations caused by an increase in

local oxygen use and subsequently blood flow due to brain activity [2]. Fast neu-

ronal signals are typically measured by EEGs, while slow haemodynamic signals are

typically measured by fMRI.

A Near-Infrared spectrophotometry system was selected as this paper’s subject

because it combines three of the author’s interests; imaging, optics, and the brain.

Additionally, the project could be done fairly cost effectively, costing roughly $200-

300.

## 1.2 Definition

The main scope of this project is to measure brain activity in a patient. In order to

do this, near infrared spectrophotometry will be used, wherein near-infrared light is

CHAPTER 1. INTRODUCTION

shown into the patient’s head to measure changes of oxygenation that directly relate

to brain activity.

The objective of this project is to design a near infrared spectrophotometry (NIRS)

system for the measurement of brain activity in localized areas in the brain. A

prototype of the design will be built and wirelessly interfaced with a computer. The

time-varying haemodynamic signals will then be plotted on the computer versus time.

It is important to note that the results will be qualitative rather than quantitative

as a device that correctly measures the optical properties of the patients skin, skull,

fat, etc is not in the scope of this project. Since these optical properties vary based

on skin pigmentation, age, gender, and many other factors, such a device is needed to

obtain exact quantitative measurements. However, without this device a NIRS system

can still measure varying haemodynamic signals. The absolute haemodynamic signal

values will be irrelevant, the change in the haemodynamic signals over time are the

relevant measurements.

Since a major target of NIRS systems are neonatal infants, it is critical to minimize

distress by performing the measurements as comfortably as possible due to the frailty

of newborns [2]. This is achieved by not having wires attached from the system to

a computer, so as to not confine movement. Additionally, since neonatal infants are

small, the system should also be small and light to restrict the infant as little as

possible. As such, the device should be portable, light, small, and wireless.

Additionally, a portable, light, small, wireless device allows the device to used on

freely moving subjects. This allows the device to measure brain activity in athletes

during exercise, subjects in social environments, and in animals.

As with most projects, especially at the undergraduate level, it is important to

CHAPTER 1. INTRODUCTION

keep costs down. Since NIRS systems for brain imaging is a fairly new field with

no currently available commercial systems, low-cost devices will help to bring NIRS

devices to the general population. In order to compete with current EEG systems,

the device has to be fairly cheap and affordable. Therefore, while many early NIRS

systems required the use of lasers, this project will focus on using low-cost LEDs.

Safety is always a concern in any device, specifically in medical equipment. The

use of LEDs help to make NIRS systems suitable for clinical environments. The use

of Lasers in early systems brought in safety concerns pertaining to damage the eye.

Thus, this project will focus on building a prototype of a low-cost wireless, portable

NIRS system that is able to measure the change in haemodynamic signals.

# Chapter 2

# Literature Review

While there are a variety NIRS devices out there, it is still very much in the research

phase, though the theory behind it is well proven. Generally, there are two classes of

NIRS systems used for brain imaging, LED based systems and Laser based system.

All the original ones used lasers as a light source. However, as time moved on it was

realized a cheaper, more convenient, safer alternative had to be found to be applicable

in the clinical market. LEDs was the solution to this. They allows for a much cheaper

system without the hassle of the optic cabling or the danger of lasers. Laser systems

are still used today though, as they still provide advantages to LEDs. They have a

much more narrow spectrum, allowing for more accurate results. They can emit a

much stronger light intensity, allowing them to penetrate deeper into tissue. As such,

two past NIRS devices will be discussed.

CHAPTER 2. LITERATURE REVIEW

## 2.1 Laser Based System

Laser based NIRS system have been around for quite some time. However, there are

still quite a few being designed today. One such design being designed quite recently

can be seen in [4]. The system is an Laser based multi-channel multi-wavelength

NIRS system.

The advantage to on such design is it has a high acquisition frequency of 1 MHz,

a very high sensitivity, a high penetration depth, a high spatial resolution, the ability

to have up to 64 channels and 18 sources, and a high temporal resolution of 25 ps

(higher than that of LEDs). One interesting thing about this paper is that is uses

time-resolved NIRS sampling, opposed to the continuous wave NIRS sampling, most

NIRS systems use. This allows the system to find the absorption and scattering coef-

ficients individually. Continuous wave NIRS sampling can only find the combination

of absorption and scattering coefficients.

The disadvantages to this system are basically the same as any Laser based system.

It is highly expensive, requiring a spaghetti of optical wires (refer to Figure 2.1).

The system is large an very much not portable. It is somewhat delicate, relying on

Photomultiplier tubes.

## 2.2 The MCP II

The MCP II is a versatile, multi-channel NIRS instrument. It was designed in order

to map neuronal activation in neonatal and adult brains in response to motor, tactile,

and visual stimulation. It aimed to have high SNR, good spatial sampling, and good

clinical useability and ease of transportation [3].

CHAPTER 2. LITERATURE REVIEW


Figure 2.1: Picture of a probe used in a Laser NIRS system. Note that this is not the system described above. [5]

CHAPTER 2. LITERATURE REVIEW

The MCP II used three LEDs to calculate the change in concentration of oxy-

haemoglobin and deoxyhaemoglobin, opposed to the more common dual wavelength

approach. They also used PIN photodiode’s with a very large activation area, with

7.5mm²
, as their detectors. This is a very good idea. PIN photodiodes are especially

sensitive, but with the addition of the large activation area it allows for a higher SNR

[3].

The sensor designed in this system is fairly interesting. A flexible sensor that was

molded with a curvature was used to fit neonatal heads as well as adults. Silicon and

SMD devices were used to prevent light leakage. Transparent silicon was also placed

around the photodiodes to provide two optical windows [3].

The system is such designed that it is able to use 8 sensors at one time, with the

ability to simultaneously measure the light intensity at two detectors. The system uses

time multiplexed data acquisition with an oversampling ADC of 12-bits, to achieve a

100Hz sampling rate. Interestingly, the system is coupled to a stimulation unit that

provides tactile, acoustic, and visual stimuli to the patient to accurately measure

brain activity [3].

The MCP II achieved very good results, obtaining a high SNR, high sensitivity,

good resolution, and a good clean signal, as can be seen in Figure 2.2. Additionally,

it is very convenient to have a multi-channel system that can simultaneously capture

two channels [3].

While, the MCP II is this projects main influence, it does have some downfalls.

The system is using an unnecessarily powerful processor, running Linux, just to pro-

vide wired network communication. A simple pic18 can be used to provide network

communication and be much cheaper. Additionally, the system is wired, making the

CHAPTER 2. LITERATURE REVIEW

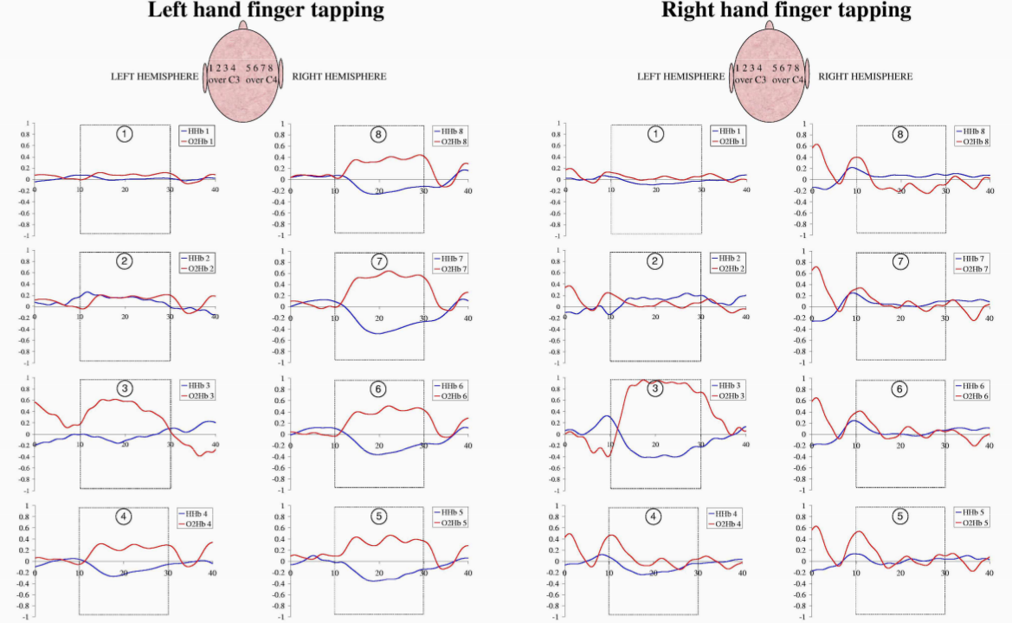
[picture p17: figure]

Figure 2.2: The MCP II measuring brain activity in the motor cortex in relation to finger tapping. ”Finger tapping exercises were performed from second 10 to 30 (dotted box). The first (sensors 1-4) and the second column (sensor 5-8) measured over left and right hemisphere respectively before, during, and after left hand finger tapping. The third (sensors 1-4) and fourth column (sensor 5-8) show the left and right hemisphere during right hand finger tapping. An activation typically consists of an increase in oxyhemoglobin (O2Hb) concentration and of a decrease in deoxyhemoglobin (HHb) concentration. The higher O2 consumption in the activated area is immediately overcompensated by an increase in blood flow, which leads to the observed pattern. Both hands showed a stronger contralateral activation on the motor cortex hemisphere. The ordinates are scaled to mol/l.” [3]

CHAPTER 2. LITERATURE REVIEW

system not very portable. Additionally, while the system is ’portable’, it is more

less transportable, rather than portable. Due to the number of channels used and

the complexity of the system, it is fairly large, though comparatively small compared

to Laser NIRS systems. The ideas used in the system are not original, but they

successfully chose a myriad of good ideas to implement an excellent working system.

## 2.3 Wireless Miniaturized NIRS System

There have been similar LED based system designed that are wireless, smaller, and

lighter. These designs are basically simplified designs of the MCP II, while producing

comparable results to other NIRS systems. One such design is [2]. The main aspect

of this design was to produce an lightweight, small, wireless NIRS system to minimize

distress when imaging neonatal infants.

The design is simple and efficient using a dual wavelength LED design. It uses

a an Silicon Labs 8051 type microcontroller connected to a Bluetooth module for

communication. It is also multi-channel based system the ability to connect up to 12

channels, though only four are connected in the literature [2].

The sensor design, though not ideal, is unique. They grouped together multiple

LEDs of the same wavelength to obtain a high integration density. Additionally, black

epoxy was placed around each photodiode and LED group to prevent light contami-

nation and leakage. The sensor placement is odd however, having two channels facing

opposing directions as the other two. This is perhaps the drawback of their design

[2].

They are able to obtain decent performance however, obtaining comparable results

to that of MCP II, as can be seen in Figure 2.3.

CHAPTER 2. LITERATURE REVIEW

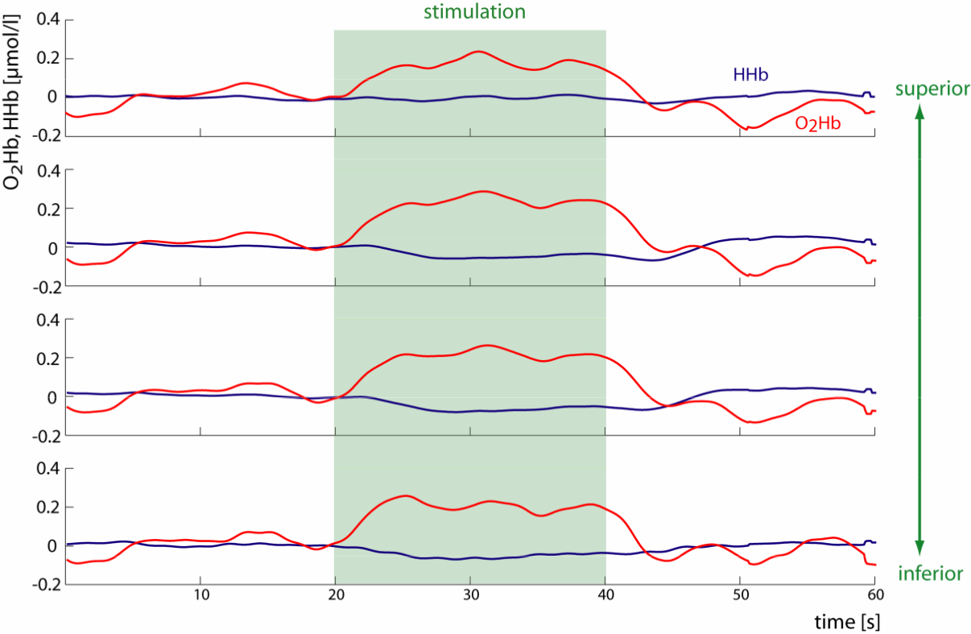
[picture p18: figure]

Figure 2.3: TheWireless Miniaturized NIRS System measuring brain activity in the motor cortex in relation to finger tapping. ”Averaged hemodynamic response of the cortex to finger tapping for four source- detector positions.” [2]

# Chapter 3

# Theory

Clearly the main problem in this project is obtaining the haemodynamic signal from

the signal light intensity measured by the photodiodes. Or, rather, turning near

infrared light into the measurement of brain activity.

## 3.1 The Basics

Analyzing the absorption spectra of light shows that the main absorbers in the near in-

frared light range (700nm - 900nm) are blood chromophores of oxyhaemoglobin (oxy-

genated haemoglobin, O2Hb) and deoxyhaemoglobin (deoxygenated haemoglobin,

HHb). Water and lipids absorb very little light, they are negligible and are basi-

cally transparent to near infrared light as depicted in Figure 3.1. Additionally it can

be seen that in this spectral range, light is weakly absorbed by the tissue, making this

spectral range ideal for NIRS imaging, which relies on reflected (backscattered) light.

Thus, any changes in light intensity shone into the body can be interpreted as vary-

ing concentration levels of O2Hb and HHb. These varying levels of oxygenation are

CHAPTER 3. THEORY

used to estimate blood volume and tissue oxygenation, which indicate haemodynamic

activity [6].

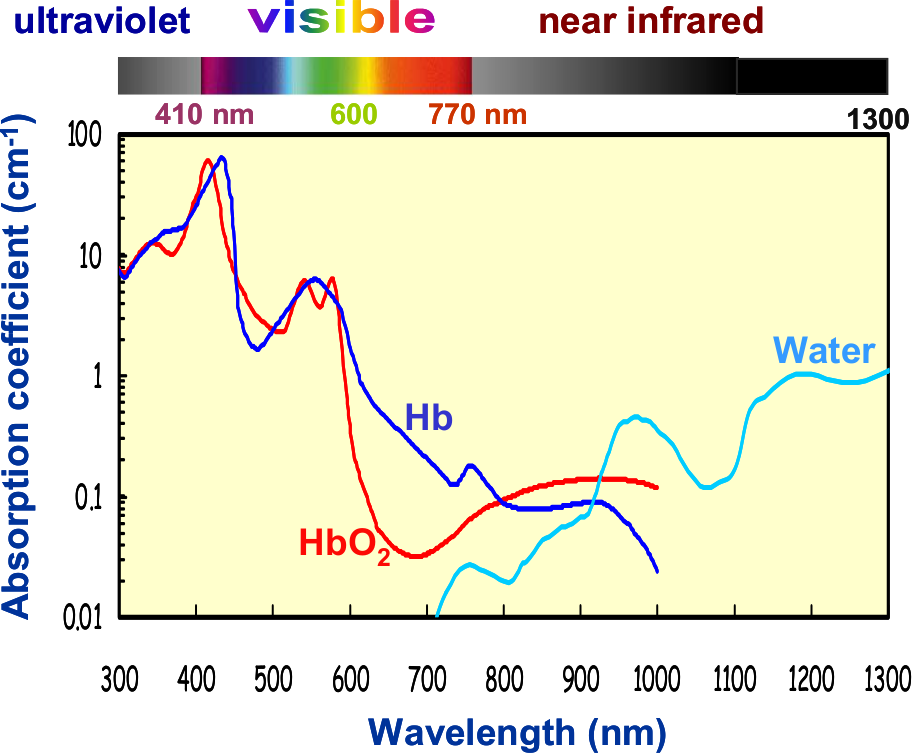
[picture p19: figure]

Figure 3.1: Absorption spectra of deoxyhemoglobin (Hb), oxyhemoglobin (HbO2), and water. The concentrations of Hb and HbO2 are set to 50 M¹

Near Infrared Light photons that are shone into the scalp are either absorbed by

varying layers of tissue, such as the skin or the skull, scatter due to interactions with

the tissue, or pass right through. Some of these scattered photons follow a kind of

banana pattern through the head and back out due to the scattering effect of tissue

(refer to figure 3.2). These backscattered photons can be picked up by a photodiode

or a similar component [6]. However, now arises the problem of turning the measured

light intensity into varying concentration levels of O2Hb and HHb.

1Sergio | Fantinis | Group, | ”Near-infrared | spectroscopy | for | the | study | of | biologi-
cal tissue,” Department of Biomedical Engineering, | Tufts University, | retrieved from
http://ase.tufts.edu/biomedical/research/Fantini/researchAreas/NearInfraredSpectroscopy.pdf

CHAPTER 3. THEORY

Figure 3.2: Propagation of photons from source to detector. The banana scattering pattern can clearly be seen here. [6]

## 3.2 Modified Beer-Lambert Law

This banana scattering effect is best described by the modified Beer-Lambert Law.

The original Beer-Lambert law, Aλ =

λ
cL, states the absorption of light (A) is

proportional to the concentration of the absorber (c) multiplied by the specific wave-

length extinction coefficient of the absorber (

λ
) and the path length the light has to

travel (L, can be seen in Figure 3.2). However, this law only holds if the photons are

absorbed or pass through the tissue in a straight line directly to the detector. Due

to higher substance concentrations and substantial light scattering, the law does not

hold in NIRS brain imaging [7].

The modified law has to take into account the longer distance of light travel and

loss of light intensity due to scattering. However, taking these into account would

no longer purely calculate the amount of light absorbed. Rather it would find the

amount of light absorbed and scattered or the total attenuation of the light, more

CHAPTER 3. THEORY

accurately called optical density which varies for a different wavelength (ODλ
) [6].

Thus, introducing signal loss due to light scattering (G), the modified Beer-Lambert

law becomes ODλ =

λ
cL + G. However, accurately measuring the path length of the

light requires expensive highly specialized instruments. Thus, the pathlength the light

has to travel can be estimated rather well by the distance between the light source and

photodetector and the wavelength dependent differential pathlength factor (DPFλ ).

That is,

L = dDP Fλ
(3.1)

where d is the distance from the light source to the photodetector (refer to Figure

3.2) [6]. Assuming there is a constant light scattering loss, taking the average of

two subsequent measurements the signal loss due to scattering (G) averages out.

Producing the modified Beer-Lambert law this project is based on [7].

∆OD =

λ

cd DP Fλ
(3.2)

Given the modified Beer-Lambert law, the light intensity measured by the photo-

diode in NIRS can accurately be described by

I = Iemittede

−ODλ
(3.3)

where Iemitted is the light emitted by the light source into the head [3, 6]. Rear-

ranging this equation gives

ODλ = ln Iemitted
I

(3.4)

CHAPTER 3. THEORY

Taking the average of the optical density (or attenuation) between two subsequent

measurements gives the equation

∆OD = ln Iemitted
I2

− ln Iemitted
I1

= ln I1
I2

=

λ

cd DP Fλ
(3.5)

where I1 is the first measurement and I2 is the subsequent measurement [8]. Since

it is well documented that the main chromophores in blood that react to the near

infrared light spectra are oxyhaemoglobin and deoxyhaemoglobin, finding the optical

density in these cases is described by

∆OD = ln I1
I2

= (

λ
O2Hb∆c

λ
O2Hb +

λ
HHb∆c

λ
HHb)d DP Fλ | (3.6)

where ∆ c is the change in concentration of the specific chromosphore [9]. Now

if the attenuation of light (Optical Density) is measured at two different wavelengths

λ1 and λ2, the above equation can be rearranged to yield

∆cO2Hb =

λ1

HHb

∆ODλ2
dDP Fλ2
−

λ2
HHb

∆ODλ1
dDP Fλ1

!

λ1
HHb

λ2
O2Hb −

λ2
HHb

λ1
O2Hb

(3.7)

∆cHHb =

λ1

O2Hb

∆ODλ2
dDP Fλ2
−

λ2

O2Hb

∆ODλ1
dDP Fλ1

λ1
O2Hb

λ2
HHb −

λ2
O2Hb

λ1
HHb

(3.8)

giving us the change in concentration between two measurements for oxyhaemoglobin

and deoxyhaemoglobin [9, 8]. This can further be extended to find oxygenation of

the blood and blood volume [6];

OXY = ∆cO2Hb − ∆cHHb | (3.9)

CHAPTER 3. THEORY

BV = ∆cO2Hb + ∆cHHb | (3.10)

It is important to note however the modified Beer-Lambert law used to derive the

above equations is based on two assumptions: the absorption of the tissue changes

homogeneously, and the light intensity lost due to scattering is constant. These

assumptions are not true in practice. However, with appropriate wavelength selections

for the light sources, these errors are minimal and negligible [9]s.

It has been shown in past studies that brain activity as a result of a specific

stimulation produces a highly localized increase in local oxygen consumption directly

followed by an increase in blood flow within a few seconds, changing the O2Hb and

HHb concentrations [10]. Thus, we can conclude that changes in O2Hb and HHb

relate to brain activity.

# Chapter 4

# Design Procedures

To create the NIRS system, a sensor consisting of LEDs, to emit light through the

area of interest, and photodiodes, to convert the transmitted incident light into an

electrical signal, must be made. The signal from the photodiodes must then be

connected to an ADC in order to convert the analog signal to a digital signal that

is readable by the computer doing the calculations. The digital signal must then be

transmitted to the computer where calculations would be done.

To control the LEDs and convert the analog signal to a digital one, a microcon-

troller will be used. The microcontroller will then be interfaced to a computer through

UART, initially through USB, then finally wirelessly through Bluetooth. The overall

system can be seen in Figure 4.1.

Bluetooth was selected over a low power wireless interface, such as ZigBee, due

to Bluetooth being widely available on all modern phones. It was the intention

to interface the device with a mobile phone, time permitting. However, this was

never done. Bluetooth consumes much more power than other competing wireless

communication systems, so to obtain optimum battery life it is not ideal. Had the

CHAPTER 4. DESIGN PROCEDURES

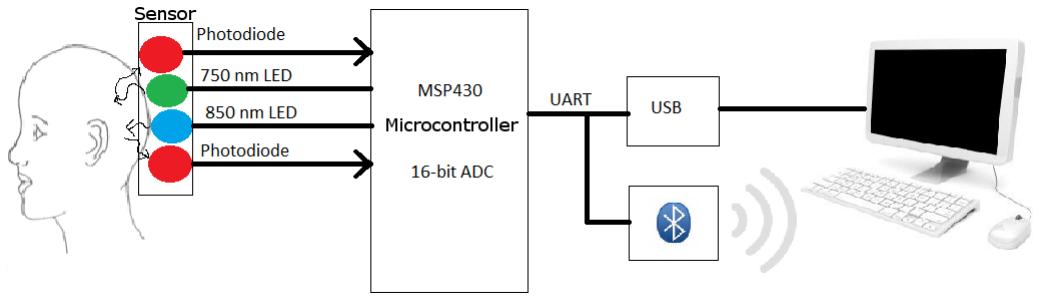
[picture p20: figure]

Figure 4.1: A very basic overview of the system. For the testing phase, USB will be used to communicate with the computer. Eventually, Bluetooth will be used as the primary means of communication.

author realized that there would be no time to interface the device with a mobile

phone, a lower power wireless communication system would have been selected, most

probably ZigBee.

To design the NIRS system, it was decided to design everything from scratch.

The microcontroller circuit, the sensor, as well as the software was designed and

built/written. This was done to truly test the author’s knowledge obtained from his

years at McMaster University. Additionally, this project provided an excellent chance

to be introduced to microcontroller circuit design.

Development of this system began with the microcontroller, since nothing would

work without it, followed by the sensor, then finally the software.

## 4.1 The Microcontroller

The microcontroller selected for use in this project is the Texas Instruments MSP430,

specifically the MSP430f4250. The MSP430 was chosen due to its low power require-

ments and 16-bit sigma-delta ADC. In most cases, a 12-bit ADC would be sufficient,

CHAPTER 4. DESIGN PROCEDURES

but a higher resolution will allow for the weak temporal signals to be detected easier.

The MSP430 is also fairly cheap. These characteristics make it ideal for this project

and made it standout from other competitors.

While the MSP430f4250 is slightly excessive for this project, due to its built in

LCD controller and array of I/O ports, it was the cheapest MSP430 model that the

minimum required I/O ports and a 16-bit ADC.

While the MSP430f4250 does not have any dedicated UART hardware on-board,

a software timer UART is sufficient in this project. The project only requires sam-

ples to be transmitted from the microcontroller to a computer. It was decided that

flow control was not necessary for this project. This decision, however, led to many

problems during testing, which will be discussed later.

To design the microcontroller circuit, datasheets, user guides, application notes,

and reference designs were read and used as a basis. Thankfully, the MSP430 has

many built in capacitors and resistors (for example, adjustable oscillator capacitors)

that help to reduce the overall components of the build. The schematic of the device

can be seen in Figure 4.2

A 32.768 Khz crystal is used because that is the only crystal the MSP430f4250 is

designed to use. It is used as somewhat as a watchdog timer, waking the MSP430

up at select intervals to see if there is work to be done, unless it is told otherwise.

Capacitors between VCC and GND were placed as close the the microcontroller as

possible, as per Dr. Doyle’s suggestion. This helps to reduce any noise that may have

been picked up between the power supply and the microcontroller. This is especially

a problem with the MSP430, any fluctuations/noise in the power supplied to it will

cause the ADC to be very noisy. This is perhaps the main reason why the MSP430

CHAPTER 4. DESIGN PROCEDURES


Figure 4.2: The schematic of the overall system. Note that two sensors are included in the diagram. The TPS79433 LDO regulator was used instead of the TPS780330220 in the diagram

CHAPTER 4. DESIGN PROCEDURES

is not very popular in projects that require signal acquisition. However, with proper

consideration, this should not be much of an issue. To further reduce the noise in

the ADC, separate power and ground are used for digital signals and analog signals,

VCC & GND and AVCC & AGND respectively.

The frequency the microcontroller operates at is governed by the voltage supplied

by its power supply. Since the Bluetooth module operates at 3.3V and the USB

UART device outputs power at 3.3V when powered by USB, a 3.3V power supply

was selected. This sets the frequency of the microcontroller to 7 Mhz, which is set by

a FLL (frequency-locked loop). The speed the microcontroller operates at is of no big

importance in this project. The sampling rate for data acquisition is slow enough, at

100Hz, that the 32Khz crystal is fast enough to supply the clock at which to sample

the data. The speed of the UART is what is affected by the microcontroller speed.

It was determined that the speed of the UART must be at least 76 800 bit/s or 76.8k

baud (see Appendix A), which is easily exceed with a clock 7Mhz.

To supply this voltage, 3 AA batteries connected to a regulator were chosen for

long battery life. An LDO (low-dropout) regulator was selected over a more tradi-

tional regulator, such as an LM317. An LDO regulator was chosen because LDO

regulators are highly efficient, consume very little power, and have low quiescent

current, increasing battery life. Due to the the low power-requirements of every com-

ponent, not much current is required by the system, making an LDO regulator ideal

for use. LDO regulators are limited to the amount of current they can output due to

consuming very little power.

The LDO regulator selected to do the job is the Texas Instruments TPS79433.

It outputs voltages at 3.3V at a maximum current of 250mA. Additionally, it can

CHAPTER 4. DESIGN PROCEDURES

be supplied power at less than 3.3V and will still output power at 3.3V. This is a

nice feature because when the batteries drain to below 3.3V, the unit will still be

operational. This regulator was selected because it meets all the requirements and

free samples were obtainable from Texas Instruments. The circuit for the power

supply was derived from the datasheet.

To interface with the computer, the an USB to UART device was used. The FTDI

FT232 was selected due to many good reviews on the device and good compatibility

with Linux and Windows. The circuit design is based on the reference design given in

the datasheet. One thing to note is that, while the built-in bootloader implemented

flow control, which was necessary to invoke the bootloader, the software UART used

in this project did not. As such, the DTR wire had to be disconnected from the

microcontroller when not programming the device. Otherwise, the DTR wire would

reset the device when communicating with the computer. The USB UART interface

was used to program the device and initially communicate to the device during testing.

Once everything was deemed working, the Bluetooth module was added to in-

terface with the computer. The Bluetooth module selected was RF-BTMX417 by

MDFLY. This was selected due to its cheap price, Bluetooth 2.0 specifications, and

low power requirements. The design for the Bluetooth module was based on the

reference design in the datasheet.

Once all the parts were selected, the majority of the necessary parts were ordered

from Digikey due to their cheap prices. Free samples were obtained of the micro-

controller and LDO regulator from Texas Instruments. The Bluetooth module was

ordered from ebay. The prototype was built on a breadboard using SMD to DIP

adaptors for each component needing one. The prototype can be seen in figure 4.3

CHAPTER 4. DESIGN PROCEDURES

Figure 4.3: Picture of the prototype

CHAPTER 4. DESIGN PROCEDURES

To program the device, the MSP430f4250 has a a built-in non-overwritable (with-

out JTAG) bootloader that can be programming over UART. A JTAG programmer

would have cost at least $100, greatly increasing the cost of this project, though

making debugging much easier. The mspgcc tools included software, written by de-

velopers at TinyOS, to write to the bootloader on the MSP430. The mspgcc toolchain

was used to compile the software, specifically mspgcc-4.4.3, and then programed to

the device using the TinyOS software.

## 4.2 The Sensor

The sensor was first designed by selecting the components. The main problem was

sourcing the LEDs with the desired wavelengths. After many emails to various distrib-

utors and manufactures, it was discovered Marubeni Corporation sold 750nm SMD

LEDs in low quantities. The epitex SMT750-25 to be exact. As such, 750 nm LEDs

were selected as one light source.

The wavelength of the other LED light source, must be above 800nm and be such

that it minimizes interference between the two LEDs. Based on the study done in

[4], the LEDs with wavelengths of 750nm and 850nm were selected to minimize inter-

ference between each LED. The 750nm wavelength responds better to deoxygenation

in the blood and the 850nm wavelength responds better to oxygenation in the blood.

Luckily enough, the 850nm LEDs were easily sourceable from Digikey in SMD form.

The OSRAM SFH4650 being the only 850nm LED easily obtainable, or rather only

800 - 870nm SMD LED easily obtainable. The OSRAM SFH4650 has very recently

been replaced by the more efficient SFH4651, while still providing similar specifica-

tions.

CHAPTER 4. DESIGN PROCEDURES

Unfortunately, the spectral half width of the LEDs are broader than desired. The

750nm LEDs have a spectral half-width of ± 35nm. While the 850nm LEDs have a

spectral half-width of ± 42nm. This means the effective wavelength may vary by the

spectral half-width, causing cross-talk between the LEDs and possibly throwing off the

calculations. They have narrow halfangles, however, ± 25◦ and ± 20◦
, respectively,

which is desired to limit light leakage and force the highest light intensity towards

the area of interest. With a forward current of 100mA, it is assumed the approximate

penetration depth of these LEDs is 1cm, based on past studies [6].

The LEDs are the most power-hungry device in this system. They could not be

directly driven by the microcontroller. NPN transistors were selected to do this task.

Specifically, the 2N4401 600mA NPN general purpose transistor. The 2N4401 was

selected as it was the cheapest transistor available at Digikey with greater than 200mA

continuous collector current. Each led has a maximum forward current of 100mA, so

to power the LEDs at their maximum intensity, a 200mA transistor would be needed.

The microcontroller would turn the NPN transistor on when it was desired to turn

its subsequent LED on. Setting the Base of the NPN transistor to high, would allow

current to flow from the Collector to the Emitter. Setting the Base to low (GND),

would stop the current from flowing from the collector to the emitter. For a high

integration density, each sensor and each transistor would have 2 LEDs of the same

wavelength. This can be seen in Figure 4.4.

To detect the reflected light back, a photodiode must be used. However, the elec-

trical signal measured by a photodiode varies in current, opposed to voltage as most

ADCs work. As such, the current must be converted into corresponding voltage by a

transimpedance amplifier. An interesting solution to this problem is the OPT101 by

CHAPTER 4. DESIGN PROCEDURES

Figure 4.4: The schematic of controlling one wavelength of LED on the sensor

Burr-Brown. It is a monolithic photodiode with a built-in transimpedance amplifier,

all in a small DIP-8 package. This makes it ideal for this project. Two photodiodes

are placed on each sensor to pick up scattering and increase the overall surface area

of the detectors.

The overall design of the sensor can be seen in Figure 4.5. It was decided that the

transistors would be put on the PCB rather than on the sensor to reduce the size of

the sensor.

Figure 4.5: The schematic of one sensor.

CHAPTER 4. DESIGN PROCEDURES

### 4.2.1 Building the sensor

Building the sensor was a daunting and hard task. The sensor had to be flexible to

adhere to the head of the patient. As such, a flexible PCB is desired over a ridged

one.

To create the flexible PCB, the toner transfer method of homemade PCB creation

was used. The PCB mill in the IEEE student Branch is not able to mill such a thin

layer of copper on a flexible surface, and especially not with such thin tracings.

The basic idea behind the toner transfer method is to print the design onto glossy

paper using a laser printer. Melt the toner onto the copper board using an iron or

something equally hot. Then etch the board using an enchant such as Ferric Chloride.

Then to remove the toner from the PCB using a solvent such as acetone.

Dupont generously supplied a sample of dual sided Pyralux Copper PCB. How-

ever, making dual sided PCBs is no trivial task using the toner transfer method. My

initial attempts to do so proved fatal. As such, one side was used a a ground plane,

while the other side was etched. Since the LEDs were surface mount, all the devices

had to be surface mount, unless they were to be mounted on the opposite side.

To create the toner mask, Cadsoft EAGLE was used. The schematic was laid out

in EAGLE, then the PCB designed. The idea was to minimize the size, keep the LEDs

as close to the photodiodes as possible, and keep the parts somewhat symmetric to

its double, while only making traces on one side. This layout sets the source-detector

distance to be about 1cm (needed solve equations 3.7 and 3.8). The result can be

seen in Figure 4.6.

The layout was then mirrored and printed out onto thick glossy photo paper

(Staples Photo Plus Gloss Paper to be exact) using a Brother laser printer with toner

CHAPTER 4. DESIGN PROCEDURES

Figure 4.6: The pcb layout of the sensor, not mirrored.

usage set to high. The Brother laser printer is all that I had on hand, an older model

laser printer would have been ideal since the Brother laser printer toner have a high

melting point, making it hard to melt the toner from the paper onto the copper.

The glossy paper was then placed onto the copper board and ironed with a standard

household clothes iron set to high. The iron was left on for about 15 minutes. After

which, the iron was removed and the copper board placed into water to separate the

paper from it. After about 10 minutes, the remaining paper was peeled off of the

copper board by hand.

The toner was now stuck to the copper board. Any broken traces were touched

up with a Sharpie marker. The opposite side (the ground plane) was coloured black

to prevent the enchant from eating away at it. The board was then submerged in

the etching solution (Ferric Chloride) to remove the exposed copper. After about 20

minutes, the exposed copper was removed and the board fully etched. The board was

then rinsed off in water and cleaned up with acetone to remove the toner and Sharpie

marker from the board. Any extra copper traces were scraped off. Solder was placed

onto the copper traces to prevent oxidation and make soldering the components easier.

The PCB was then complete as can be seen in Figure 4.7.

Unfortunately, I made the traces to thin. While the came out okay out of the

etchant, after many bends, some traces broke (even though they appeared fine).

Again, the majority of the electrical components were obtained from Digikey.

CHAPTER 4. DESIGN PROCEDURES

(a) Sensor after etching
(b) Sensor showing flexibility

Figure 4.7: The completed sensor PCB

CHAPTER 4. DESIGN PROCEDURES

With the exception of the OPT101 monolithic photodiode, which was obtained from

Texas Instruments as a free sample. After populating the sensor and difficult task of

adding jumper wires, the finalized sensor prototype was complete. Correctly building

the board took quite a few hours to complete. The complete sensor can be seen in Fig-

ure 4.8. Due to time constraints only 1 sensor was built. Though, the microcontroller

was designed to handle 2.

## 4.3 Software

To write the software for the microcontroller, C was selected over assembly to reduce

development time and increase readability. As discussed above, the UART function

had to be written in software in addition to data acquisition. To do this, exam-

ple timer UART code by L. Westlund at Texas Instruments, available in the IAR

Embedded Workbench example files, was used as a basis for the software UART

functionality. This was done because the author did not know how to implement the

UART functionality from scratch. Once UART was working, data acquisition was

tackled.

### 4.3.1 Data Acquisition

Due to the slow haemodynamic response in your brain due to activity, a time res-

olution of 10ms (or 100Hz) is all that is needed. That is all the wavelengths and

positions must be sampled at least every 10 ms.

To do this, data is sampled in a time multiplexed fashion. That is, all the data is

sampled independently in a certain order within the time resolution.

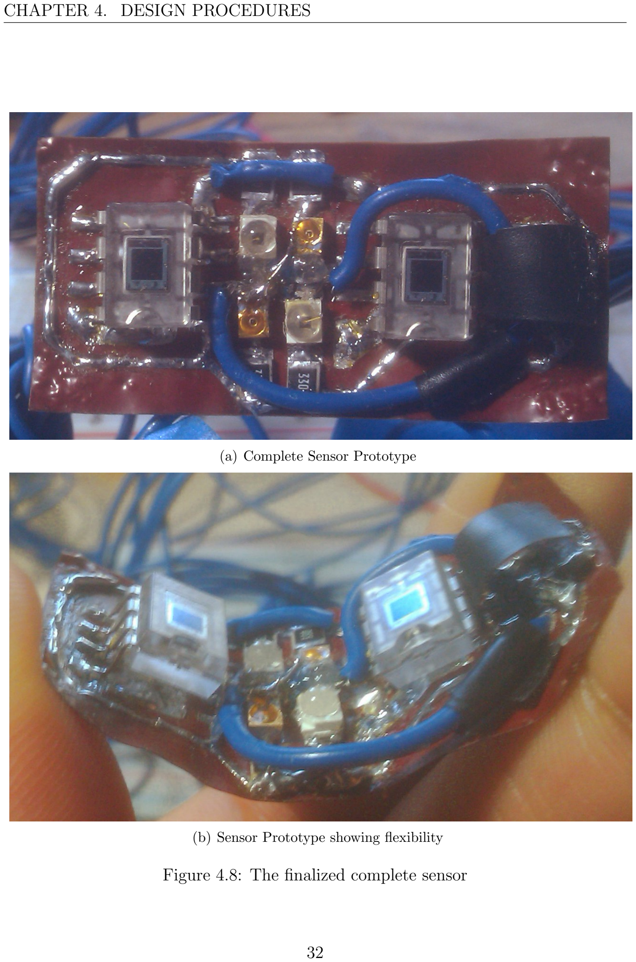
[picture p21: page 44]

CHAPTER 4. DESIGN PROCEDURES

(a) Complete Sensor Prototype
(b) Sensor Prototype showing flexibility

Figure 4.8: The finalized complete sensor

CHAPTER 4. DESIGN PROCEDURES

Firstly the sensors are sampled with all the LEDs off to obtain the background light

intensity. Then the first wavelength of LED is turned on and allowed to stabilize for

a period of time. Then the first signal is obtained from the first OPT101 photodiode,

subtracted by the background light intensity, and transmitted to the computer. Then

the second signal is obtained from the second OPT101 photodiode, subtracted by

the background light intensity, and transmitted to the computer. Then the LEDs

are turned off, the second wavelength LEDs turned on, allowed to stabilize, and

the cycle repeated. Once this cycle is completed, all the LEDs are turned off, the

background light intensity sampled, and the cycle repeats. This is illustrated in Figure

4.9. Though, perhaps it is more easily seen in the microcontroller code flow chart in

Appendix B.1.

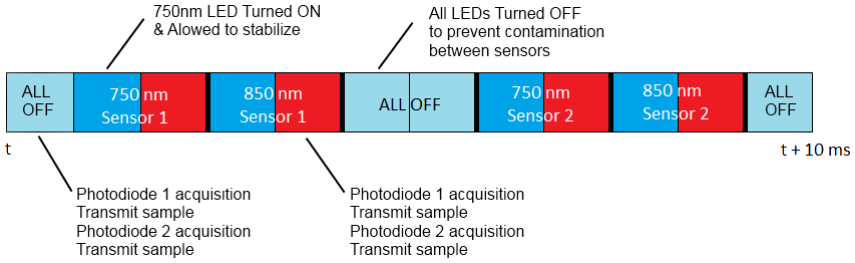
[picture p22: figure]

Figure 4.9: An illustration of the time multiplexed acquisition cycle.

### 4.3.2 Computer Software

To write the software, Ruby was selected as the language of choice. It was selected due

to the author’s desire to learn Ruby as it is a very popular dynamic general purpose

object-oriented programming language. It is spoken highly of by many experienced

computer science veterans. While not up to the speed of C or C++, Ruby has

CHAPTER 4. DESIGN PROCEDURES

amazingly good performance for a dynamic programming language.

The computer software must firstly obtain the data from the device. To do this the

serialport library from rubygems (a host of many Ruby librarys or ’gems’) was used

to interact with the serial port on the computer, communicating through UART. The

serial port is opened, sent the message ’S’, to message the device to begin acquiring

data. The program then receives the data. The data is split into two parts the upper

8 bit and the lower 8 bits when it is received. The program combines them together

and divides the resulting value by 0xFFFF. The reason for this is the output from the

ADC on the microcontroller is relative to its maximum value of 0xFFFF. To ensure

the data arrives correctly, an ’S’ is transmitted by the device before sending each

set of data to ensure that the device is synchronized correctly with the computer.

Once all the data is received, the calculations are done on the raw data to obtain the

necessary relevant values.

Equations 3.7 and 3.8 were used to calculate the change in concentrations. Equa-

tion 3.6 was used to calculate the differential optical density. During the project

demonstration Equation 3.6 was not written correctly in the code, giving wrong re-

sults. This has since been fixed and the differential optical density is now calculated

correctly. In order to calculate the change in concentrations, first the specific wave-

length constant and differential pathlength factors must be found.

Since the specific wavelength extinction coefficient of the absorber(

λ
) cannot be

directly measured with near infrared light, they are found by interpolating the values

given for these coefficients for oxyhaemoglobin and deoxyhaemoglobin in literature,

specifically [11] and [12]. This results in

750nm
H b = 1.532,

750nm
O 2Hb = 0.600,

850nm
H b

= 0.781,

850nm

O 2Hb = 1.097. Calculating the differential pathlength factor (DPFλ )

CHAPTER 4. DESIGN PROCEDURES

yeilds DP F⁷³⁰nm=5.0055 and DP F⁸⁵⁰nm=4.6564. The calculation for DPFλ
can be

seen in Appendix A.2.

Once the calculations are complete the change in concentrations are output to text

files that can be read by Matlab. The data is very noisy and requires a low pass filter

to be done on it to obtain the necessary data. Due to time limitations, a low pass

filter was not able to be made in Ruby for the software. As such, Matlab was decided

to be used to filter the data. As per [3], a low pass filter with a cutoff of 0.5Hz should

be used. Therefore a low pass fourth-order butterworth filter was used with a cutoff

of 0.5Hz. The Matlab source code can be seen in Appendix C. Taking the Fourier

transform of the data before filtering gives the result in Figure 4.10(a). Taking the

Fourier transform of the data after filtering gives the result in Figure 4.10(b).

The design of the device is now complete and results can be seen.

## 4.4 Cost

Since one of the goals of this project is to low-cost, Table 4.1 shows the total cost to

build one of these systems with one sensor. The USB to UART module will be left

out since it is only needed for programming the device. In a mass produced system,

the microcontroller would be programmed by JTAG anyway.
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

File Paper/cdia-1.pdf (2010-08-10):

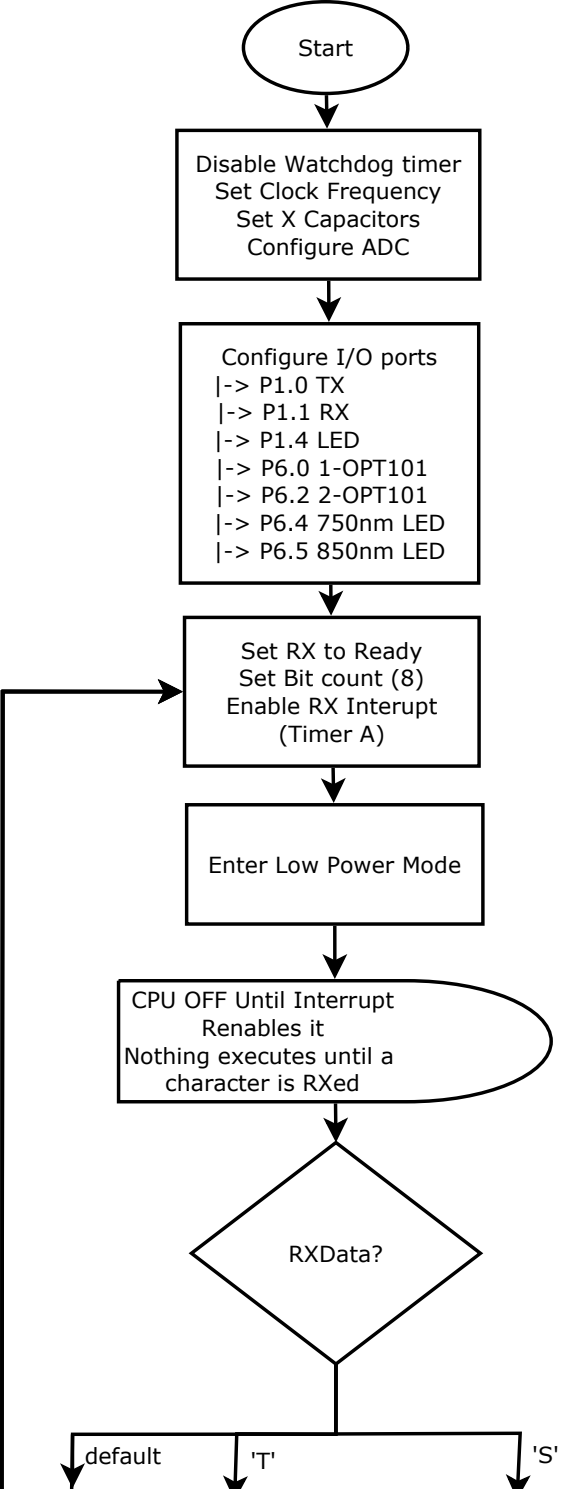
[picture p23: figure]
Start; Disable Watchdog timer Set Clock Frequency Set X Capacitors Configure ADC; Configure I/O ports |-> P1.0 TX |-> P1.1 RX |-> P1.4 LED |-> P6.0 1-OPT101 |-> P6.2 2-OPT101 |-> P6.4 750nm LED |-> P6.5 850nm LED; Set RX to Ready Set Bit count (8) Enable RX Interupt (Timer A); Enter Low Power Mode; RXData?; 'S' default; CPU OFF Until Interrupt Renables it Nothing executes until a character is RXed
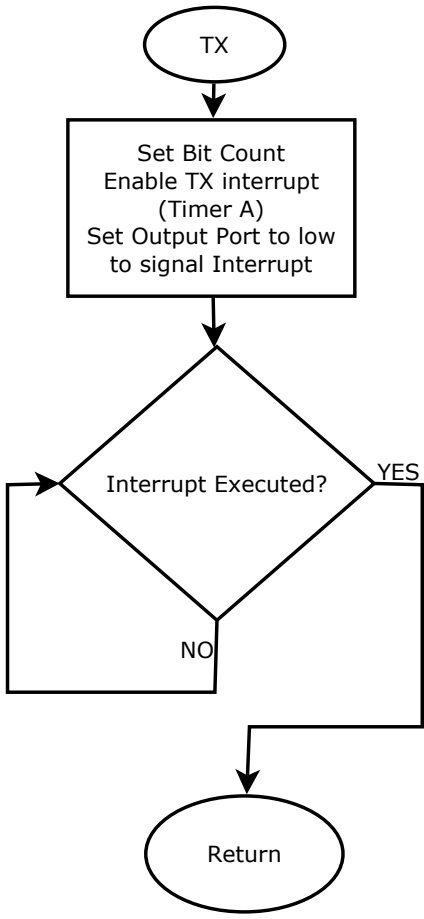
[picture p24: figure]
Set Bit Count Enable TX interrupt (Timer A) Set Output Port to low to signal Interrupt; Interrupt Executed?; Return; YES

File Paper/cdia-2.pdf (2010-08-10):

All LEDs OFF; Read sample from OPT-1 from ADC = Background Light 1; Read sample from OPT-2 from ADC = Background Light 2; 750nm LED ON; Read sample from OPT-1 from ADC; TX sample lower 8-bits TX sample upper 8-bits; YES; Capture Data sample = 2000 i=0; sleep 10/12 ms

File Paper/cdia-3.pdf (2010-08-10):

Read sample from OPT-2 from ADC; TX sample lower 8-bits TX sample upper 8-bits; 850nm LED ON; Read sample from OPT-1 from ADC; sleep 10/12 ms

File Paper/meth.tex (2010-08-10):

\chapter{Theory}

Clearly the main problem in this project is obtaining the haemodynamic signal from the signal light intensity measured by the photodiodes. Or, rather, turning near infrared light into the measurement of brain activity.

\section{The Basics}

Analyzing the absorption spectra of light shows that the main absorbers in the near infrared light range (700nm - 900nm) are blood chromophores of oxyhaemoglobin (oxygenated haemoglobin, O$_{2}$Hb) and deoxyhaemoglobin (deoxygenated haemoglobin, HHb). Water and lipids absorb very little light, they are negligible and are basically transparent to near infrared light as depicted in Figure 3.1. Additionally it can be seen that in this spectral range, light is weakly absorbed by the tissue, making this spectral range ideal for NIRS imaging, which relies on reflected (backscattered) light. Thus, any changes in light intensity shone into the body can be interpreted as varying concentration levels of O$_{2}$Hb and HHb. These varying levels of oxygenation are used to estimate blood volume and tissue oxygenation, which indicate haemodynamic activity \cite{rosen05}.
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

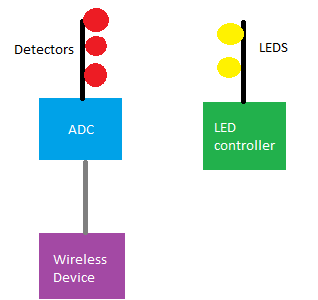
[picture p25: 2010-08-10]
Paper/block.png

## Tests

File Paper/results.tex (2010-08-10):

\chapter{Results and Discussion}

\section{Motor Movement}
Due to the high objectivity of brain activity due to motor movement, measuring brain activity due to motor movement is perhaps the best way to asses the system. Placing the sensor above the top left motor cortex (refer to Figure 5.1), and having the test subject do the 'chicken dance' (that is repeatably touching the thumb to the tip of each finger) with their right hand for 30s yields the results in Figure 5.2. Note that the subject started the 'chicken dance' at around 1s, stopped movement to see the effect, then resumed the chicken dance again, and then finally stopped movement before the end of the test.

\begin{figure}[htp]
\centering
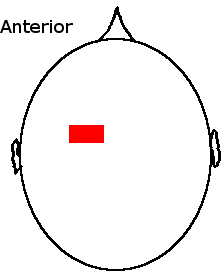
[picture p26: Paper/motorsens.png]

\caption[Placement of Sensor to Measure Right Hand Movement]{Approximate placement of the sensor to measure right hand movement. The sensor, marked in red, is positioned above the left motor cortex.}
\end{figure}

\begin{figure}[htp]
\centering
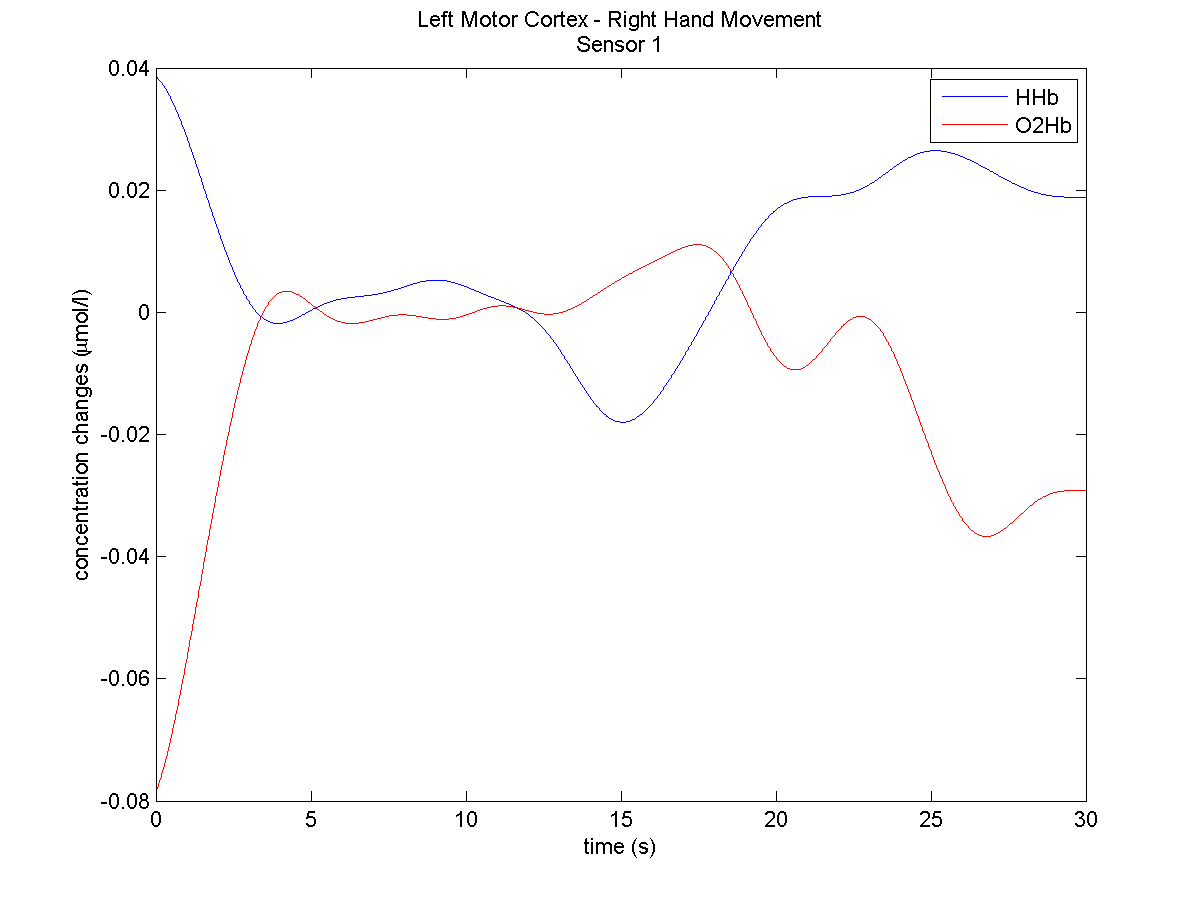
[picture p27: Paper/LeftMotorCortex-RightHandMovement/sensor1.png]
\subfigure[Sensor 1]{}
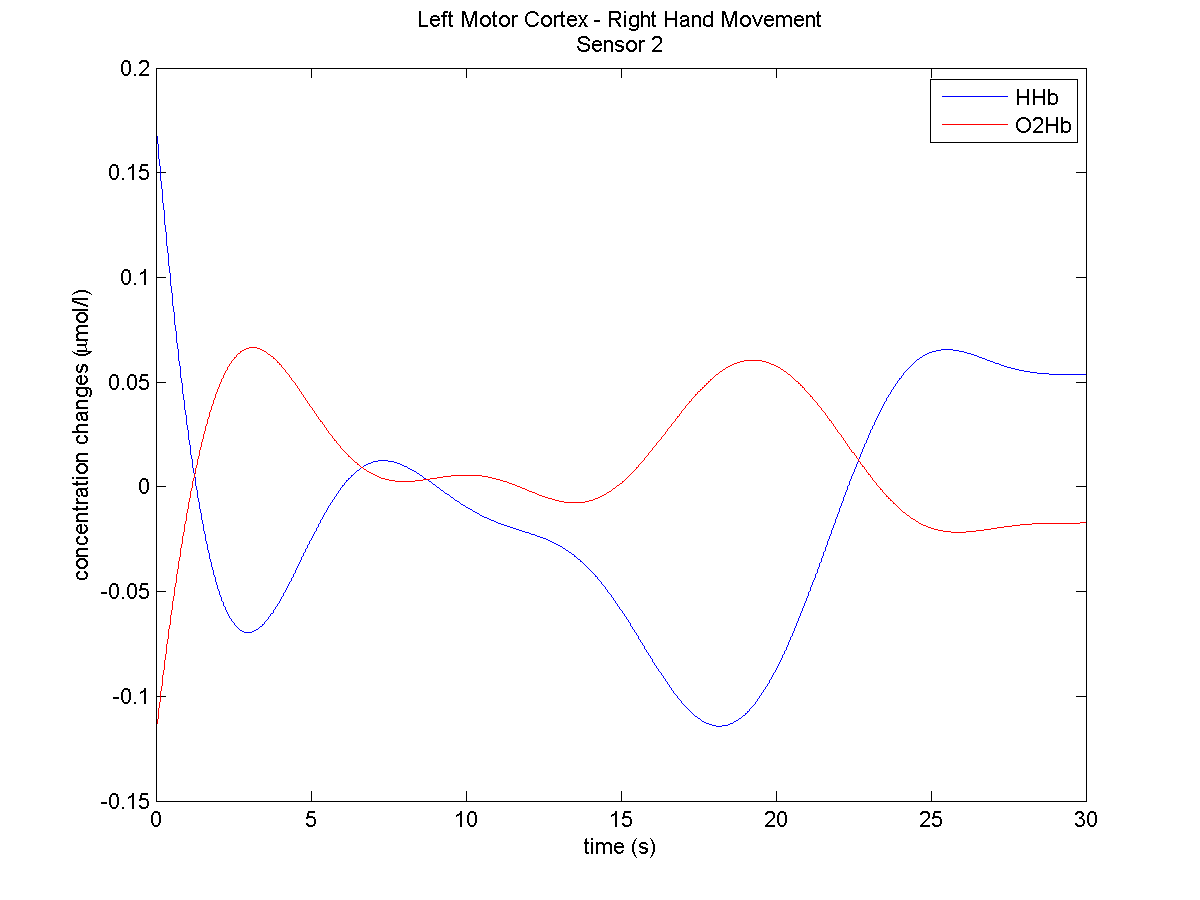
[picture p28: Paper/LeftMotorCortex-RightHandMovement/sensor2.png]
\subfigure[Sensor 2]{ }
\caption[Left Motor Cortex Measurements with Motor Movement]{The result of having the subject move their right hand with the sensor placed over the left motor cortex. The change in concentration of oxyhaemoglobin is marked in red and the change in concentration of deoxyhaemoglobin is marked in blue. The subject began the 'chicken dance' at ~1s, briefly stopped at around 7s, started the 'chicken dance' again at around 9s, and finally stopped at around 22s, as can be seen in the Sensor 2 measurements.}
\end{figure}

The measurements from Sensor 1 do not seem to be correct. It is excessively noisy, masking the haemodynamic effect of the blood perfusion that is the result of the motor movement. Perhaps, the photodiode is damaged or the lens scratched/dirty. There was not enough time to correctly trouble shoot the problem. In either case, the results from Sensor1, while it does pick up varying light intensities, contains too much noise to extract the relevant data from it. As such, the results from Sensor 1 should be ignored. However, for the sake of completeness and to correctly asses the system, figures of the measurements from Sensor 1 will still be included, though not discussed. 

Looking at the figures, it can be seen that the concentration changes at the start of the measurements, while relevant, are much larger compared to the rest. This is a result of initially measuring the system from 0, thus there is a high concentration change from the beginning. Once the correct base level is achieved, the results normalize and the exact concentration changes can be seen. Therefore, when looking at the results one can safely ignore the first few measurements. One thing to note about these measurements is that the subject had long dark hair, which will decrease the overall SNR of the system.

Analyzing at the results from Sensor 2, it can be seen that with motor activity on the right part of the body, there is an increased amount of oxyhaemoglobin concentration and a decreased amount of deoxyhaemoglobin concentration. When motor activity stops (at around 7s), the amount of oxyhaemoglobin concentration decreases and the amount of deoxyhaemoglobin concentration increases. When motor activity starts up again (at around 9s), again there is an increased amount of oxyhaemoglobin concentration and a decreased amount of deoxyhaemoglobin concentration. When the motor activity finally stops completely, the amount of oxyhaemoglobin concentration decreases and the amount of deoxyhaemoglobin concentration greatly increases. This agrees with what one would expected from neuronal activation. With neuronal activation comes an increased amount of blood perfusion, thus increased amounts of oxyhaemoglobin and decreased amount of deoxyhaemoglobin. When neuronal activation stops, blood perfusion decreases, adversely, causing decreased amounts of oxyhaemoglobin and increased amount of deoxyhaemoglobin. This also agrees with the results obtained from other NIRS systems (refer to Chapter 2, Figures 2.2 and 2.3 specifically).

To better analyze motor movement, lets have a look at the same measurements but with no motor movement. To examine the case with no motor movement, the sensor was placed in roughly the same place as in Figure 5.1 with the subject attempting to stay perfectly still. The results of this are displayed in Figure 5.3.

\begin{figure}[htp]
\centering
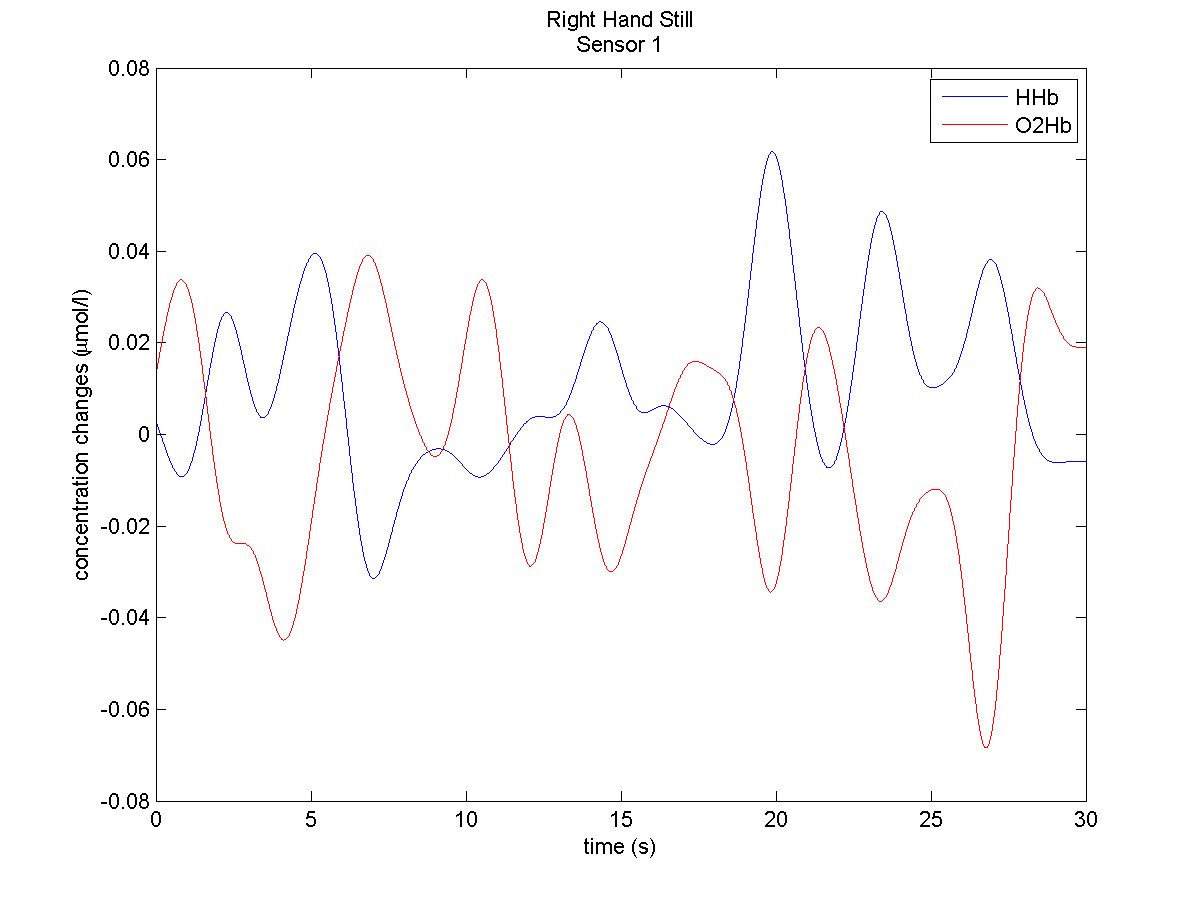
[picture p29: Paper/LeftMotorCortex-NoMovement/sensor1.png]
\subfigure[Sensor 1]{}
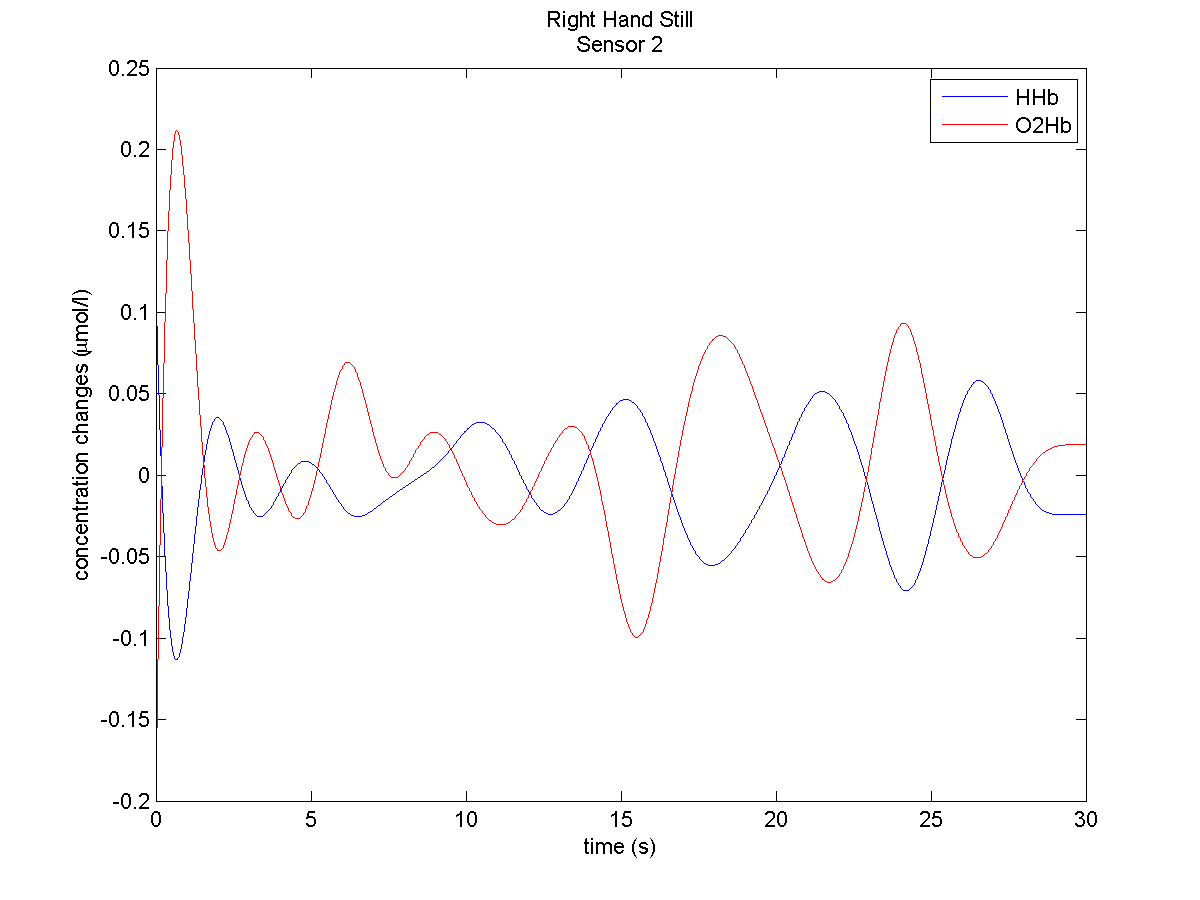
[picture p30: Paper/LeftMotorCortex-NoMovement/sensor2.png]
\subfigure[Sensor 2]{ }
\caption[Left Motor Cortex Measurements with No Motor Movement]{The result of having the subject attempt to sit still with the sensor placed over the left motor cortex. The change in concentration of oxyhaemoglobin is marked in red and the change in concentration of deoxyhaemoglobin is marked in blue.}
\end{figure}

The results in Figure 5.3 show that when the subject is at rest, there is no constant increase or decrease in oxyhaemoglobin or deoxyhaemoglobin. Rather, the change in concentration constantly increases and decreases. This is probably caused by cells in the neuron consuming oxygen, increasing the deoxyhaemoglobin concentration, but with the increased level of deoxyhaemoglobin, fresh blood enters the neuron, increasing the oxyhaemoglobin concentration. With this cycle repeating itself, the results obtained would mirror that of in Figure 5.3.

To test the repeatably of this NIRS device, the same motor movement ('the chicken dance') will be done again with the sensor in roughly the same place as in Figure 5.1. It can be seen in Figure 5.4.

\begin{figure}[htp]
\centering
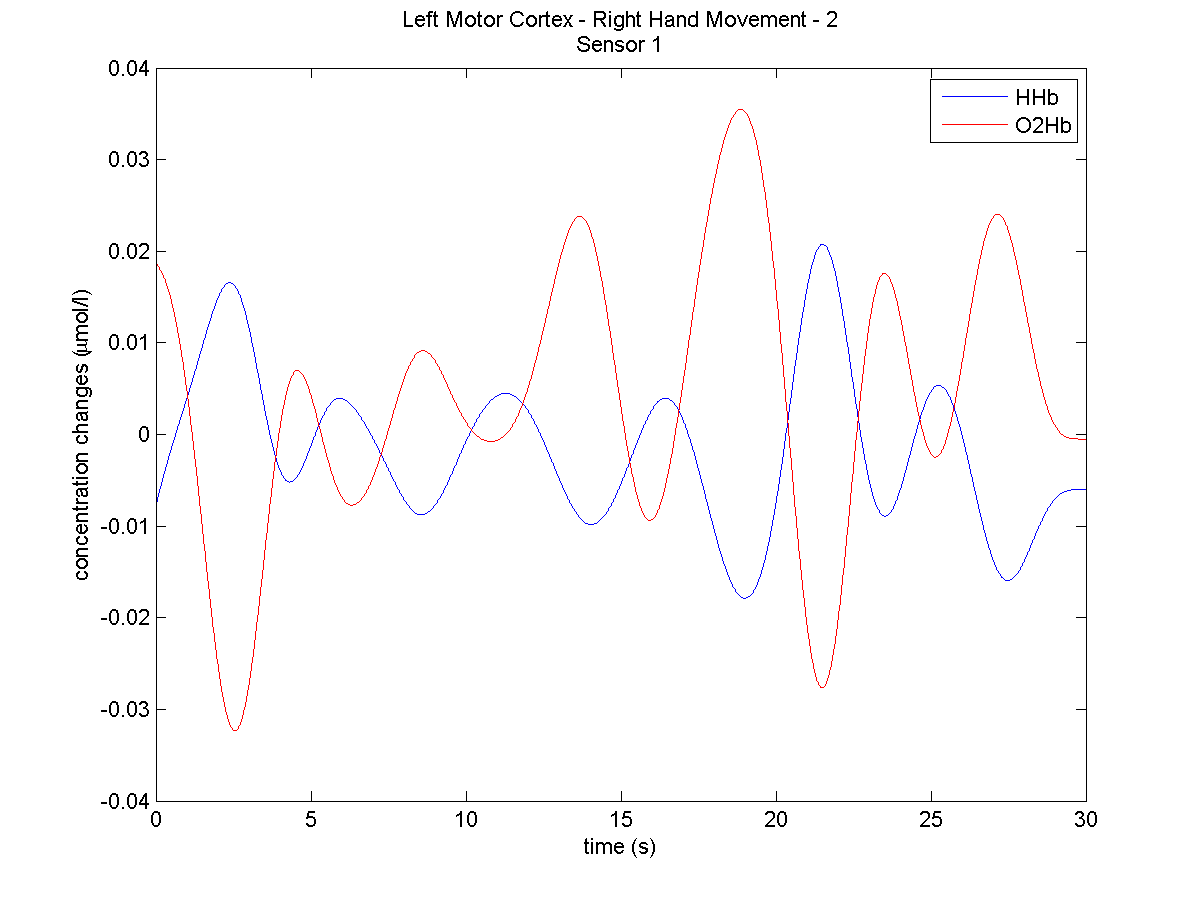
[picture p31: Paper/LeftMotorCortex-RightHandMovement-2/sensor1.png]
\subfigure[Sensor 1]{}
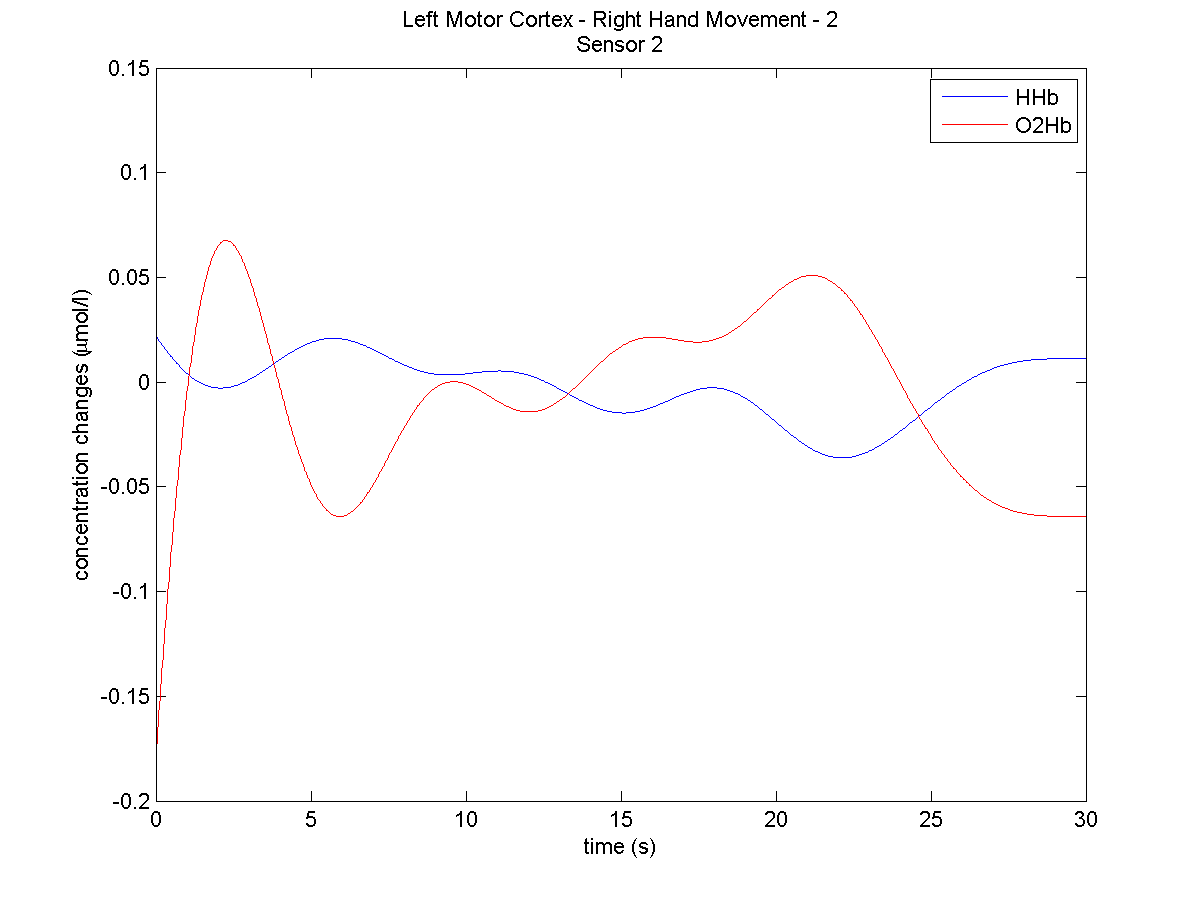
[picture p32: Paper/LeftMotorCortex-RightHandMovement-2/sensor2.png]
\subfigure[Sensor 2]{ }
\caption[Left Motor Cortex Measurements with Motor Movement, Test 2]{The second result of having the subject do the 'chicken dance' with their right hand with the sensor placed over the left motor cortex. The change in concentration of oxyhaemoglobin is marked in red and the change in concentration of deoxyhaemoglobin is marked in blue. This time the subject began movement at around 0s, stopped at around 4s, and slowly began the 'chicken dance' again at around 8s before finally stopping at roughly 25s.}
\end{figure}

The results in Figure 5.4 show a good amount of repeatability. The results agree with that in the first test of right hand motor activity. When there is motor activity on the right part of the body, there is an increased amount of oxyhaemoglobin concentration and a decreased amount of deoxyhaemoglobin concentration. When the motor activity stops, the amount of oxyhaemoglobin concentration decreases and the amount of deoxyhaemoglobin concentration increases.

Doing the same test with the left hand and the sensor placed on top of the right motor cortex (refer to Figure 5.5) gives the results in Figure 5.6.

\begin{figure}[htp]
\centering
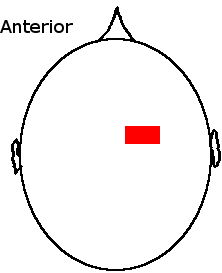
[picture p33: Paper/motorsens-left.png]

\caption[Placement of Sensor to Measure Left Hand Movement]{Approximate placement of the sensor to measure left hand movement. The sensor, marked in red, is positioned above the right motor cortex.}
\end{figure}

\begin{figure}[htp]
\centering
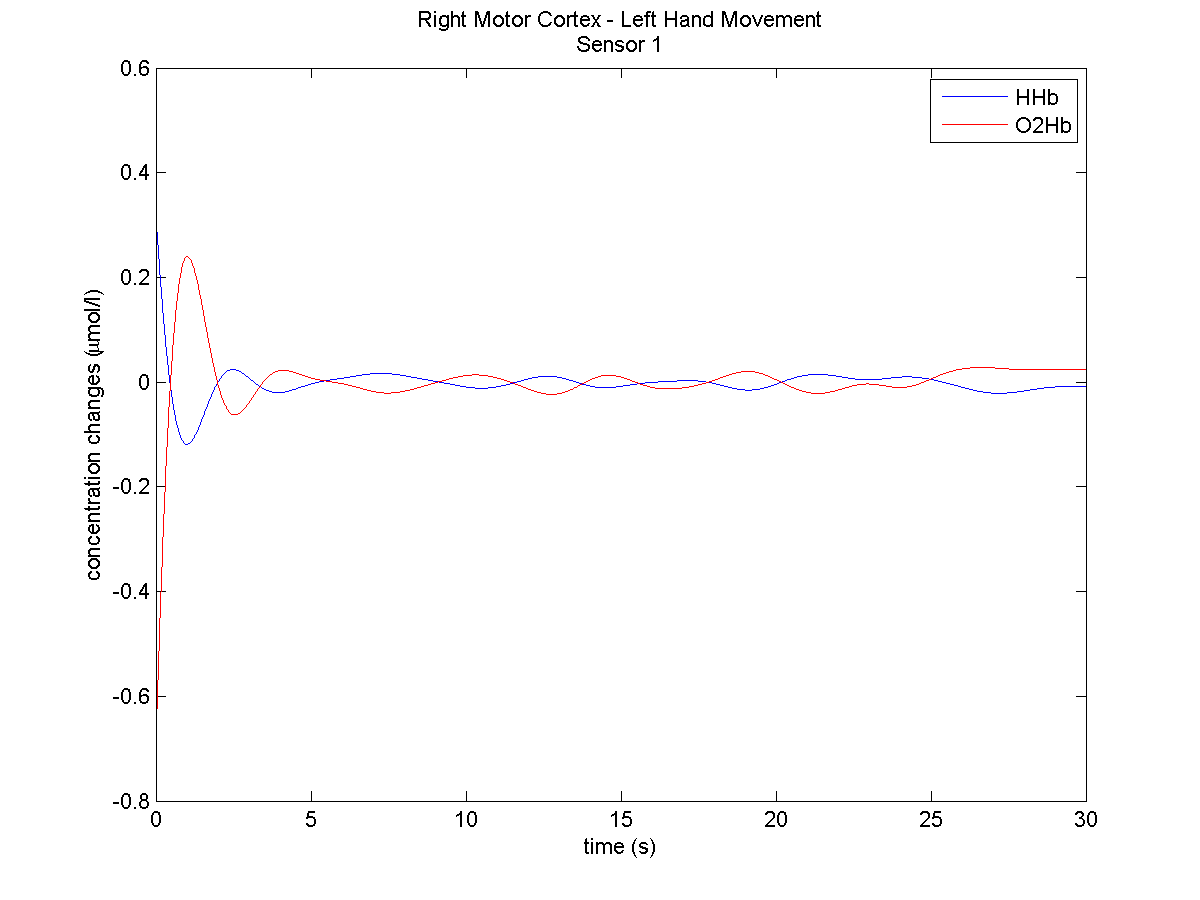
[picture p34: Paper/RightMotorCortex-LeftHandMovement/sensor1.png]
\subfigure[Sensor 1]{}
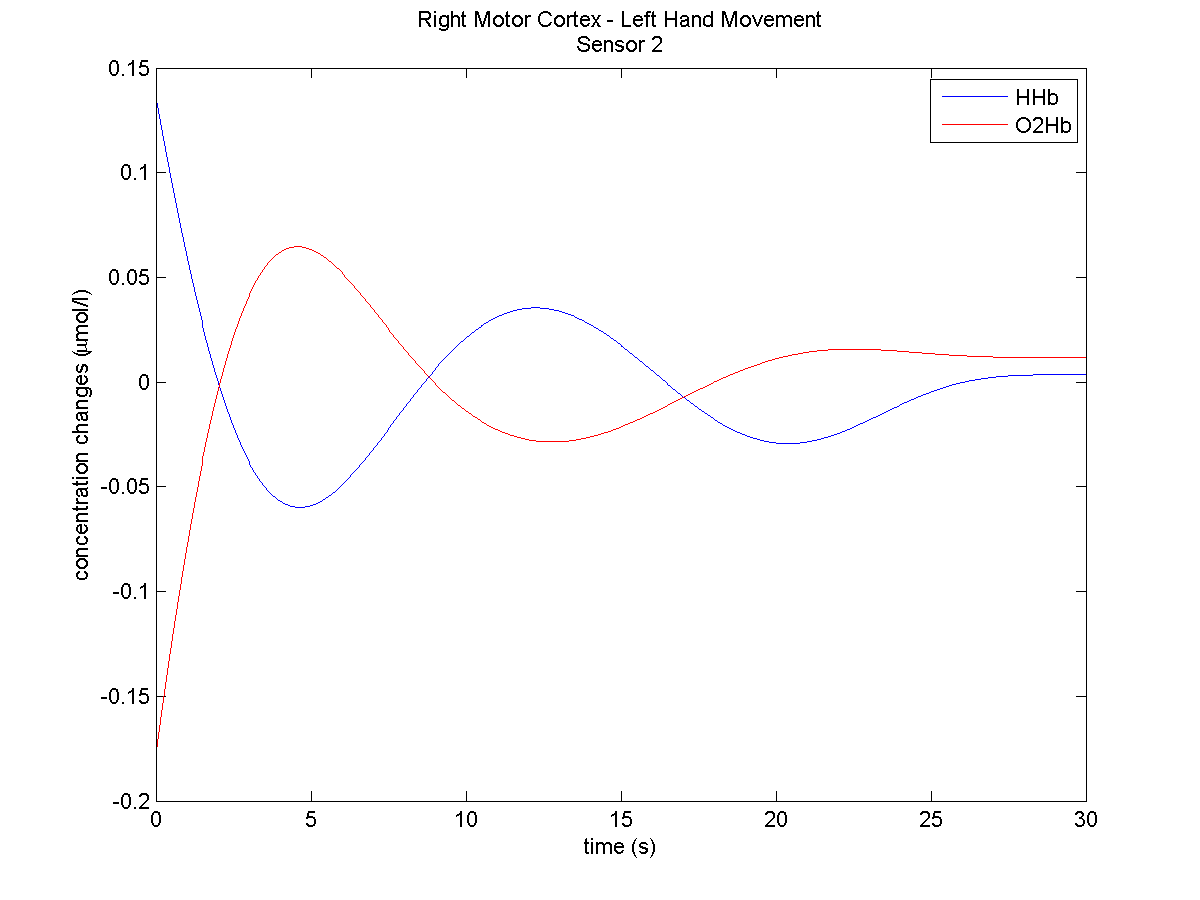
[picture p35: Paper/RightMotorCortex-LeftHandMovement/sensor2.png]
\subfigure[Sensor 2]{ }
\caption[Left Motor Cortex Measurements with Motor Movement]{The result of having the subject move their left hand with the sensor placed over the right motor cortex. The change in concentration of oxyhaemoglobin is marked in red and the change in concentration of deoxyhaemoglobin is marked in blue. The subject began the 'chicken dance' at ~0s, stopped at around 7s, and started the 'chicken dance' again at around 16s, as can be seen in the Sensor 2 measurements.}
\end{figure}

Once again, it can be seen that with motor activity on the left part of the body, there is an increased amount of oxyhaemoglobin concentration and a decreased amount of deoxyhaemoglobin concentration in the right side of the motor cortex. Once more, when motor activity stops, the amount of oxyhaemoglobin concentration decreases and the amount of deoxyhaemoglobin concentration increases.

\section{Thinking Intensely}
Now that it has been shown that the NIRS device can somewhat accurately measure brain activity, others areas of the brain can be explored. Measuring brain activity in the frontal lobe while thinking about random things can be done when the sensor is placed as seen in Figure 5.7. This yields the results in Figure 5.8. Doing the same measurements but with the subject's eyes closed and in a relaxed state with the subject trying not to think about anything yields the results in Figure 5.9.

\begin{figure}[htp]
\centering

\caption[Placement of Sensor to measure Frontal Lobe]{Approximate placement of the sensor to measure brain activity when thinking intently. The sensor, marked in red, is positioned above the frontal lobe.}
\end{figure}

\begin{figure}[htp]
\centering
\subfigure[Sensor 1]{}
\subfigure[Sensor 2]{ }
\caption[Frontal Lobe Measurements while Thinking Intensely]{The result of having the subject think intensely with the sensor placed over the frontal lobe. The change in concentration of oxyhaemoglobin is marked in red and the change in concentration of deoxyhaemoglobin is marked in blue.}
\end{figure}

\begin{figure}[htp]
\centering
\subfigure[Sensor 1]{}
\subfigure[Sensor 2]{ }
\caption[Frontal Lobe Measurements while Relaxed]{The result of having the subject not think of anything in a relaxed manor and their eyes closed with the sensor placed over the frontal lobe. The change in concentration of oxyhaemoglobin is marked in red and the change in concentration of deoxyhaemoglobin is marked in blue.}
\end{figure}

Comparing the 2 results, it can be seen that brain activity while the subject is thinking intensely can indeed by measured. When the subject is thinking intensely there is a constant increase in oxyhaemoglobin and constant decrease in deoxyhaemoglobin, showing brain activity. However, when the subject is in a relaxed non-thinking manor, the change in concentrations of oxyhaemoglobin and deoxyhaemoglobin constantly fluctuate; they are continually increases and decreasing.

\section{Visual stimulation}
Measuring the visual cortex with the subject's eyes continually moving from one intensely focused object to another, gives the results in Figure 5.11. The sensor placement can be seen in Figure 5.10. Doing the same measurements but with the subject's eye's closed, produces the result in Figure 5.12.

\begin{figure}[htp]
\centering

\caption[Placement of Sensor to Measure Visual Cortex]{Approximate placement of the sensor to measure brain activity in the visual cortex. The sensor, marked in red, is positioned on top of the visual cortex.}
\end{figure}

\begin{figure}[htp]
\centering
\subfigure[Sensor 1]{}
\subfigure[Sensor 2]{ }
\caption[Visual Cortex Measurements while Moving Eyes between focused objects]{The result of having the subject constantly moving their eyes from different intensely focused object with the sensor placed over the visual cortex. The change in concentration of oxyhaemoglobin is marked in red and the change in concentration of deoxyhaemoglobin is marked in blue.}
\end{figure}

\begin{figure}[htp]
\centering
\subfigure[Sensor 1]{}
\subfigure[Sensor 2]{ }
\caption[Frontal Lobe Measurements while Relaxed]{The result of having the subject close their eyes with the sensor placed over the visual cortex. The change in concentration of oxyhaemoglobin is marked in red and the change in concentration of deoxyhaemoglobin is marked in blue.}
\end{figure}

Interpreting these results is not quite clear. Even with the subject's eyes closed there seems to still be brain activity occurring in the visual cortex, though to a lesser degree than that when the subject's eyes were open. Perhaps there was movement of the sensor in the second measurements or possibly the subject was still moving their eyes with their eyes closed. 

Where the change in oxyhaemoglobin starts to increase and the change in deoxyhaemoglobin starts to increase in Figure 5.11 (with the subject's eyes open) is where the subject slowed down their eye movements and took longer to stare at each object. There is still brain activity occurring, but to a lesser degree than when the subject's eyes were moving fast, which is why there is a decrease in the change of oxygenation. This is a potential fatal flaw of this system. At this point it appears as if the subject closed their eyes or rather brain activity stopped occurring in this area. However, this was not the case, instead lower amount of oxygenation was required by the neuron. This is where a system that can exactly quantify the concentration would stand out from this system.

\section{Muscle Contractions}

As an addition to this project, the system was tested to see if it could measure muscle activity. Placing the sensor onto the test subject's bicep and having them continually flex and extend their bicep yields the result in Figure 5.13. Giving the subject a heavy weight and having them flex and extend their bicep again yields the result in Figure 5.14.

\begin{figure}[htp]
\centering
\subfigure[Sensor 1]{}
\subfigure[Sensor 2]{ }
\caption[Bicep Measurements with Continuous Flexion and Extension]{The result of having the subject continually flex and extend their bicep with the sensor placed over the bicep under activity. The change in concentration of oxyhaemoglobin is marked in red and the change in concentration of deoxyhaemoglobin is marked in blue. The subject stopped continuously flexing and extending their arm at around 8s, leaving it in the extended state until around 15s, where they began flexing and extending their bicep again}
\end{figure}

\begin{figure}[htp]
\centering
\subfigure[Sensor 1]{}
\subfigure[Sensor 2]{ }
\caption[Bicep Measurements with Continuous Fexion and Extension with a Weight]{The result of having the subject continually flex and extend their bicep with a heavy weight in their hand with the sensor placed over the bicep under activity. The change in concentration of oxyhaemoglobin is marked in red and the change in concentration of deoxyhaemoglobin is marked in blue. The subject began lifting the weight at 0s, became fatigued at around 6s and was unable to lift the weight, began lifting the weight again at around 11s, finally becoming fatigued at around 23s. The subject still held the weight in their hand while fatigued, continually trying to lift it.}
\end{figure}

These results prove interesting, the system can indeed measure muscle activity. With the change in oxyhaemoglobin rates increasing during muscle activity and decreasing when not under activity, similar to brain activity. Interestingly, it can be seen that when trying to lift the wight the change in concentrations is higher than when not lifting any weight. This shows that when trying to lift more weight, the muscle has an increased need for oxygen. It can also be seen that when the muscle is fatigued, rather than having the change in oxyhaemoglobin decrease to below 0 and the change in deoxyhaemoglobin increase to above 0, the change in oxyhaemoglobin is constant and a positive value. Similarly, the change in deoxyhaemoglobin is constant and a negative value. This shows the muscle still requires oxygen and oxygenated blood is still coming in trying to restore the muscle to normal, while the muscle fibres are constantly consuming oxygen.

\section{Remarks}

This system is far from perfect. Every couple of measurements will result in one bad one that is either riddled with noise or does not make any sense. However, repeating the same measurement later on may yield positive results. It has not been determined what causes this. When the results are positive, they are repeatable, though.

The system has very good battery life. Granted it is powered by three AA batteries. Throughout the entire prototyping phase, the batteries were never needed to be changed. Previous systems have shown to have a battery life of just 3 hours \cite{rosen05}. The exact battery life of the system when constantly on is unknown, it should compete favourably with those previous systems though. The system has a ridiculously long standby time, having been in standby for at least 24hours. This is all due to the low power components in the system. 

While the prototype is not portable by all definitions of the word, it is battery powered and wireless and can be easy transported for use in the field. Due to the use of the breadboard the prototype is fairly large. However, should a PCB be made for the system, it could easily be made to be 6cm by 2cm, excluding the USB to UART module. At this size, the system wold definitely be portable by all definitions of the word.

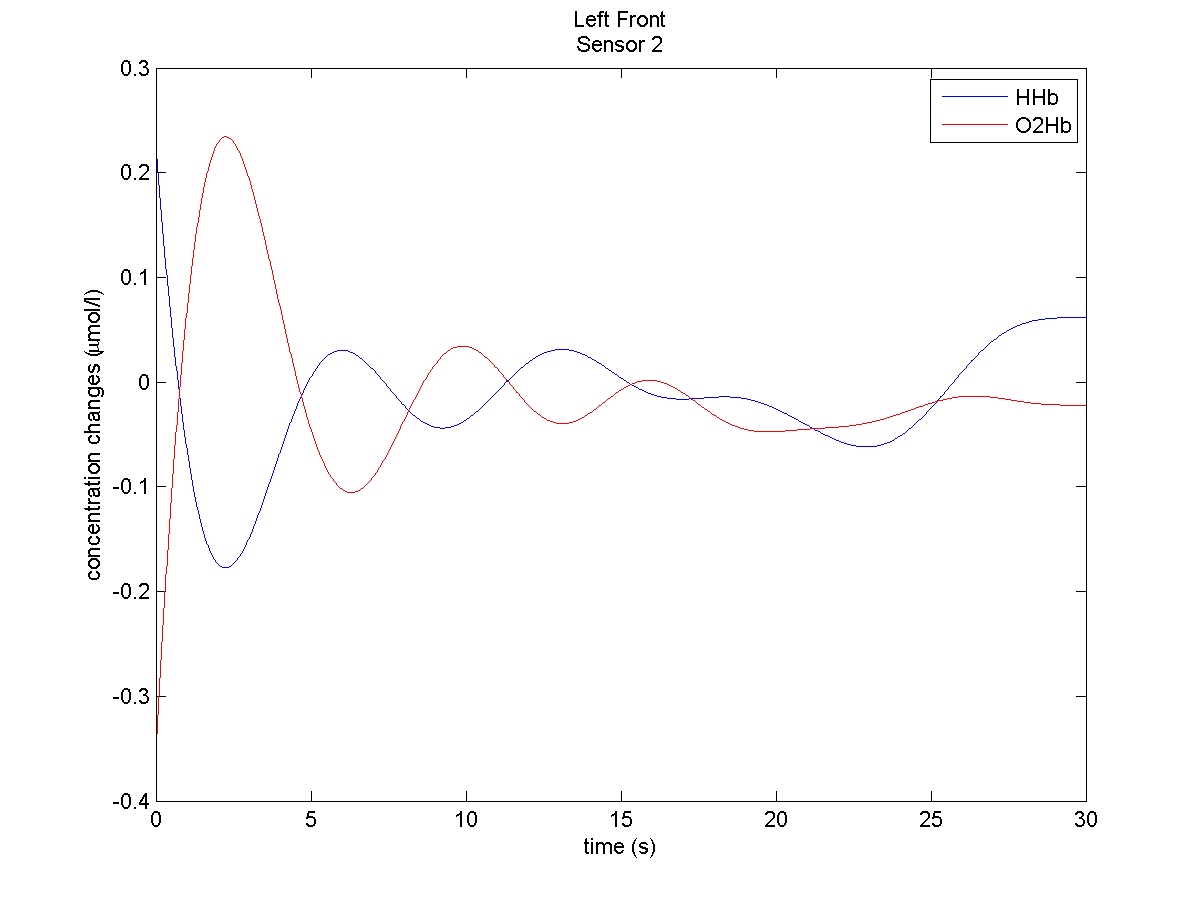
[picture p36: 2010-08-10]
Tests/back/left front/sensor2.png

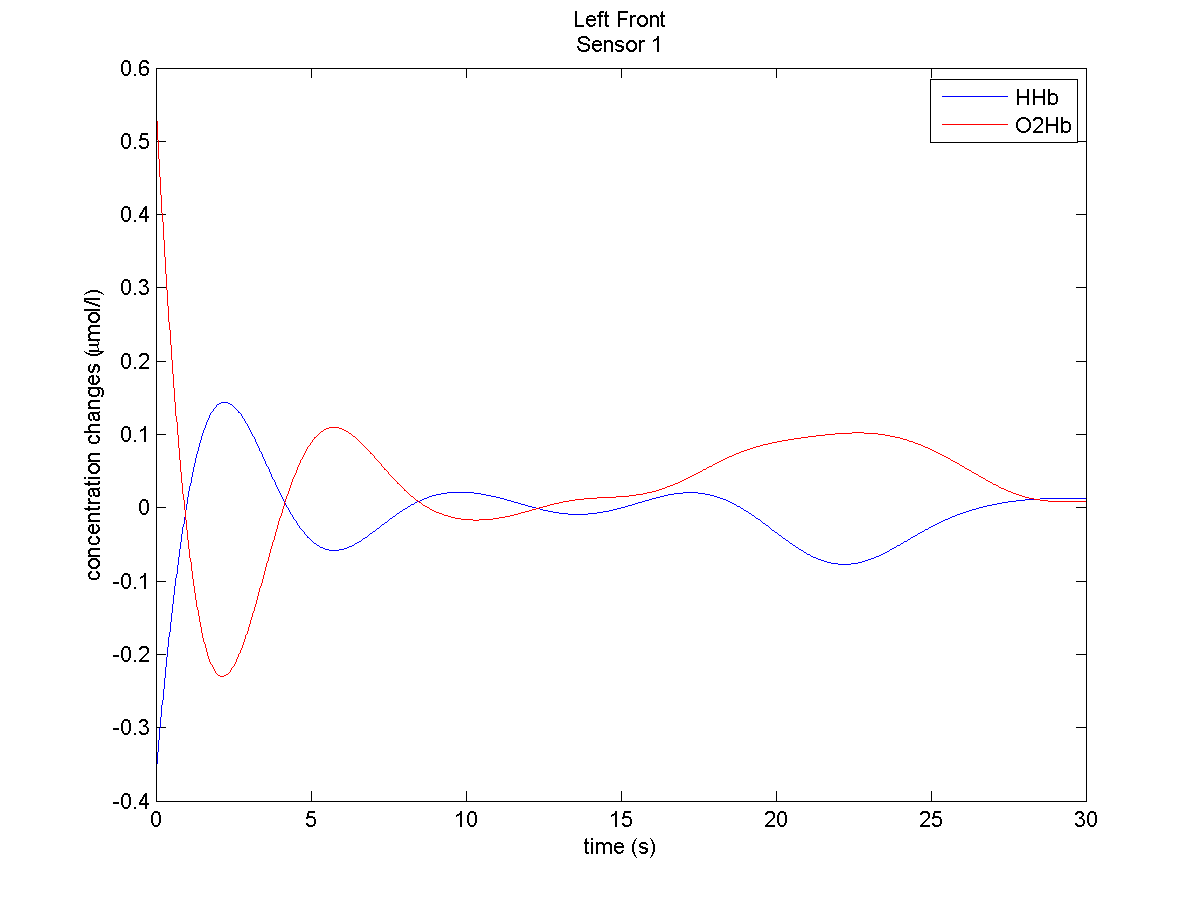
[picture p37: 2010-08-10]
Tests/back/left front/sensor1.png

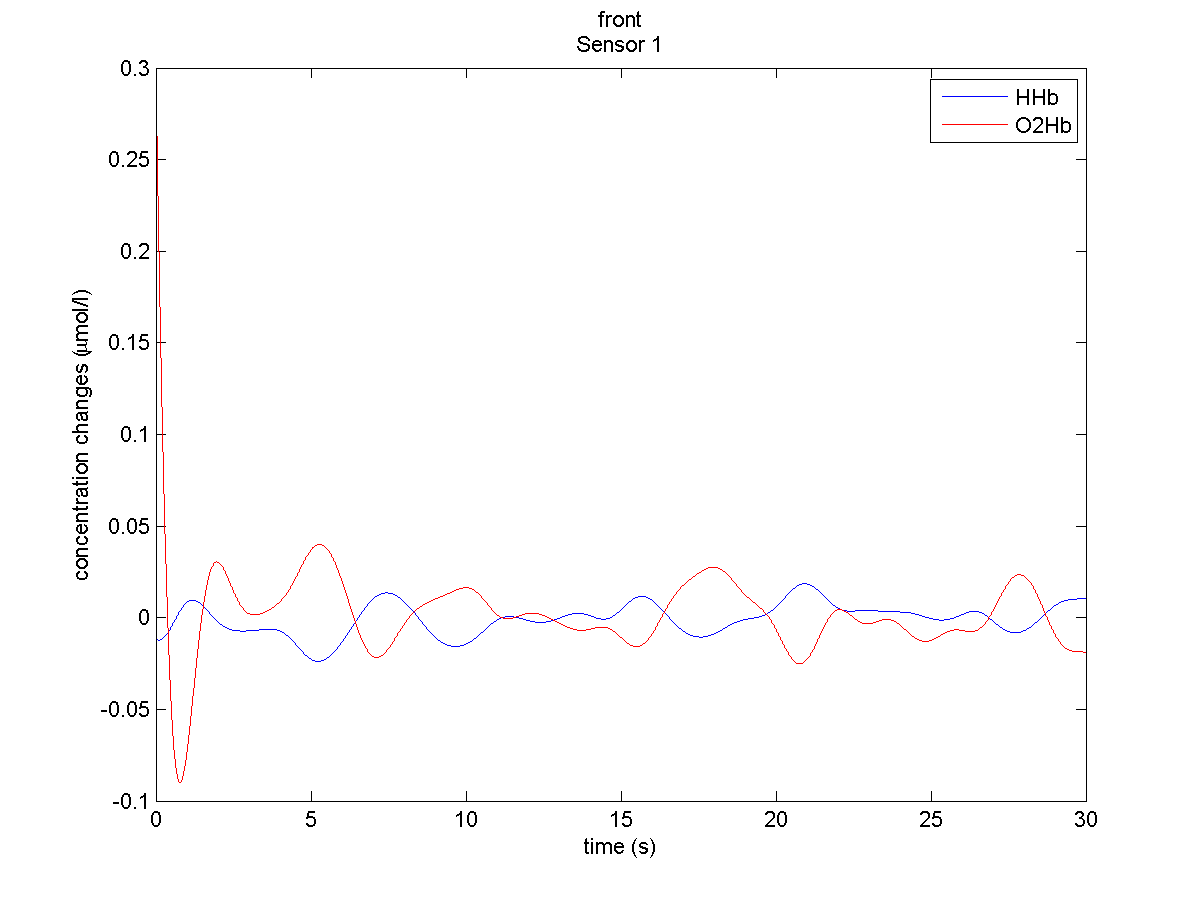
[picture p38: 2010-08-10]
Tests/back/front/sensor1.png

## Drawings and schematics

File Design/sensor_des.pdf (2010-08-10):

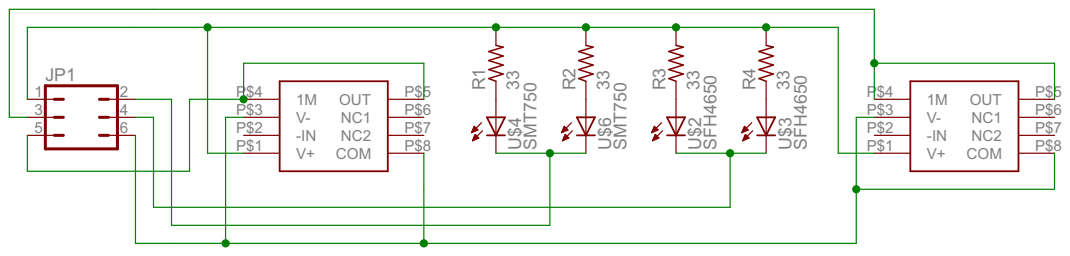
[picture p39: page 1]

SFH4650 SFH4650 SMT750 SMT75303333333 V+ P$1 -IN P$2 V- P$3 1M P$4 OUT P$5 NC1 P$6 NC2 P$7 COM P$8 V+ P$1 -IN P$2 V- P$3 1M P$4 OUT P$5 NC1 P$6 NC2 P$7 COM UP$8 $2 U$3 U$4 U$6 R1R2R3R4 1 2 JP1 3 4 5 6

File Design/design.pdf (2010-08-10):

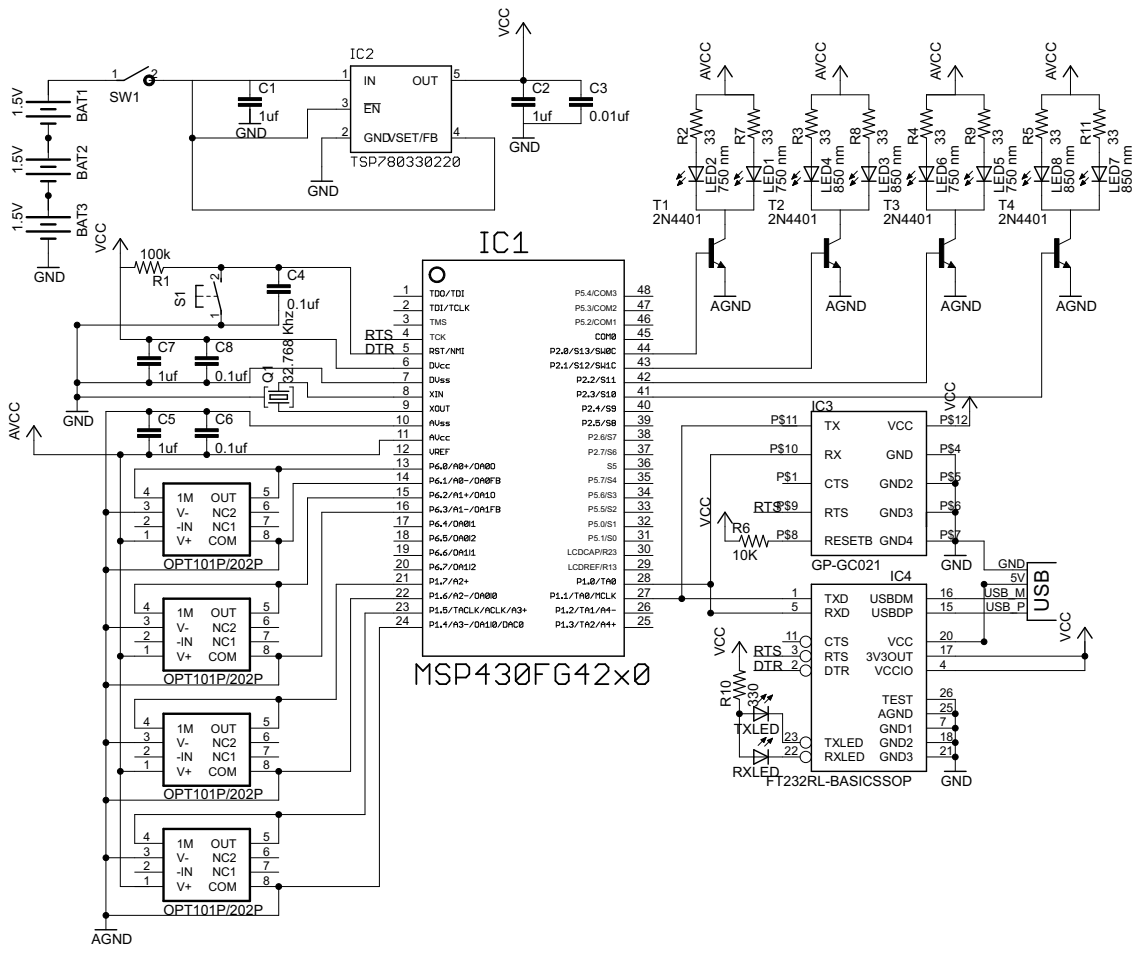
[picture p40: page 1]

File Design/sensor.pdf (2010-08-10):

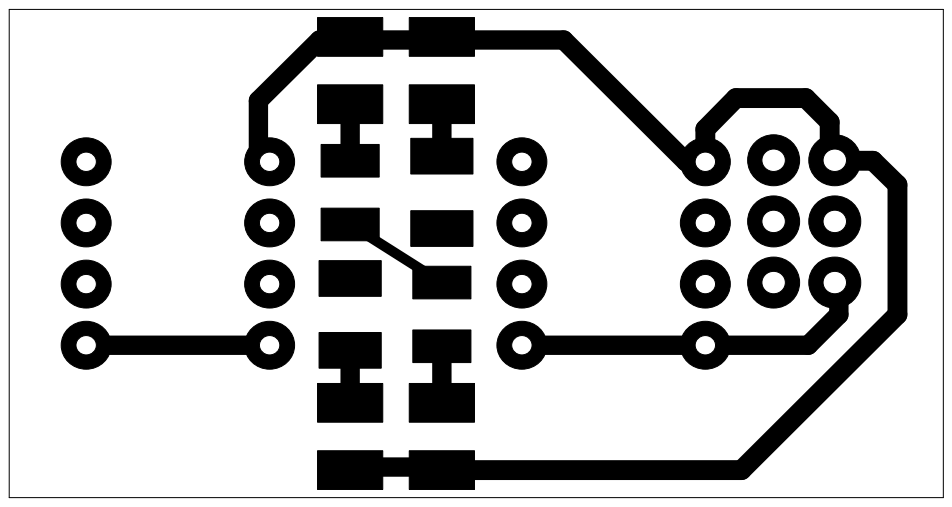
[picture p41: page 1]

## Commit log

2010-08-10 added test runs and server code and matlab filter
2010-08-10 added Eagle schematics
    [design.sch, sensor.brd, sensor.sch, sensor2.brd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]
